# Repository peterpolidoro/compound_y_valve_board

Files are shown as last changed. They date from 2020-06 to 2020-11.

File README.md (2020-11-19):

- [Repository Information](#org6a90782)
  - [Description](#orgf515803)
- [Images](#org8e21772)
- [Schematic](#org4408de4)
- [Gerbers](#org2b33e62)
- [Bill of Materials](#org6bcd28f)
  - [PCB Parts](#orgb6b8d32)
  - [Supplemental Parts](#org0a79596)
  - [Vendor Parts Lists](#orgea142e0)
- [Supplemental Documentation](#org34a7f76)
  - [Assembly Instructions](#orgbe6a6db)
- [Manufacturing Archive](#org17d4580)

# Repository Information

-   **Name:** y\_arena\_valve\_controller
-   **Version:** 1.3
-   **License:** Open-Source Hardware
-   **URL:** <https://github.com/janelia-kicad/y_arena_valve_controller>
-   **Author:** Peter Polidoro
-   **Email:** peterpolidoro@gmail.com

## Description

This board controls the y-arena valves for the Turner lab.

## Documentation

<https://janelia-kicad.github.io/y_arena_odor_controller>

# Images

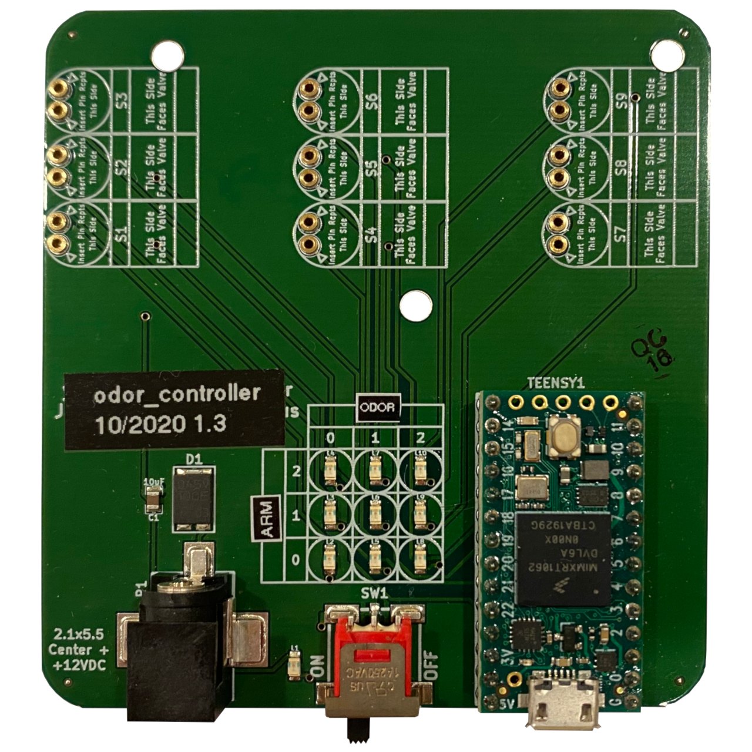
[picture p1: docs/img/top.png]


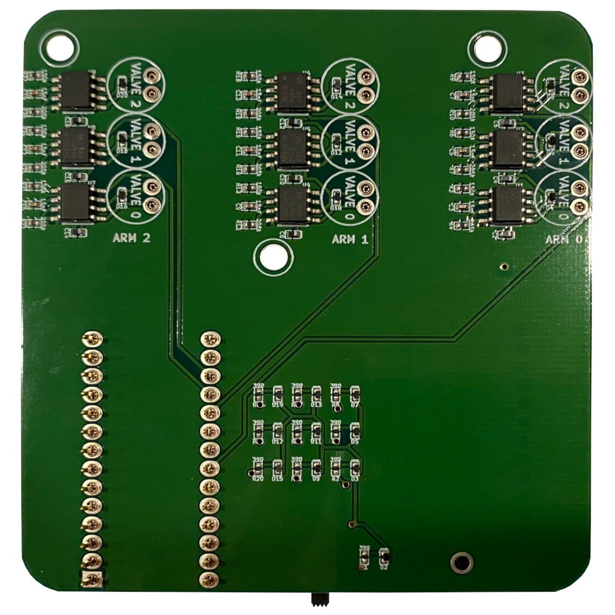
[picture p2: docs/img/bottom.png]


# Schematic

[./schematic/y\_arena\_valve\_controller.pdf](./schematic/y_arena_valve_controller.pdf)

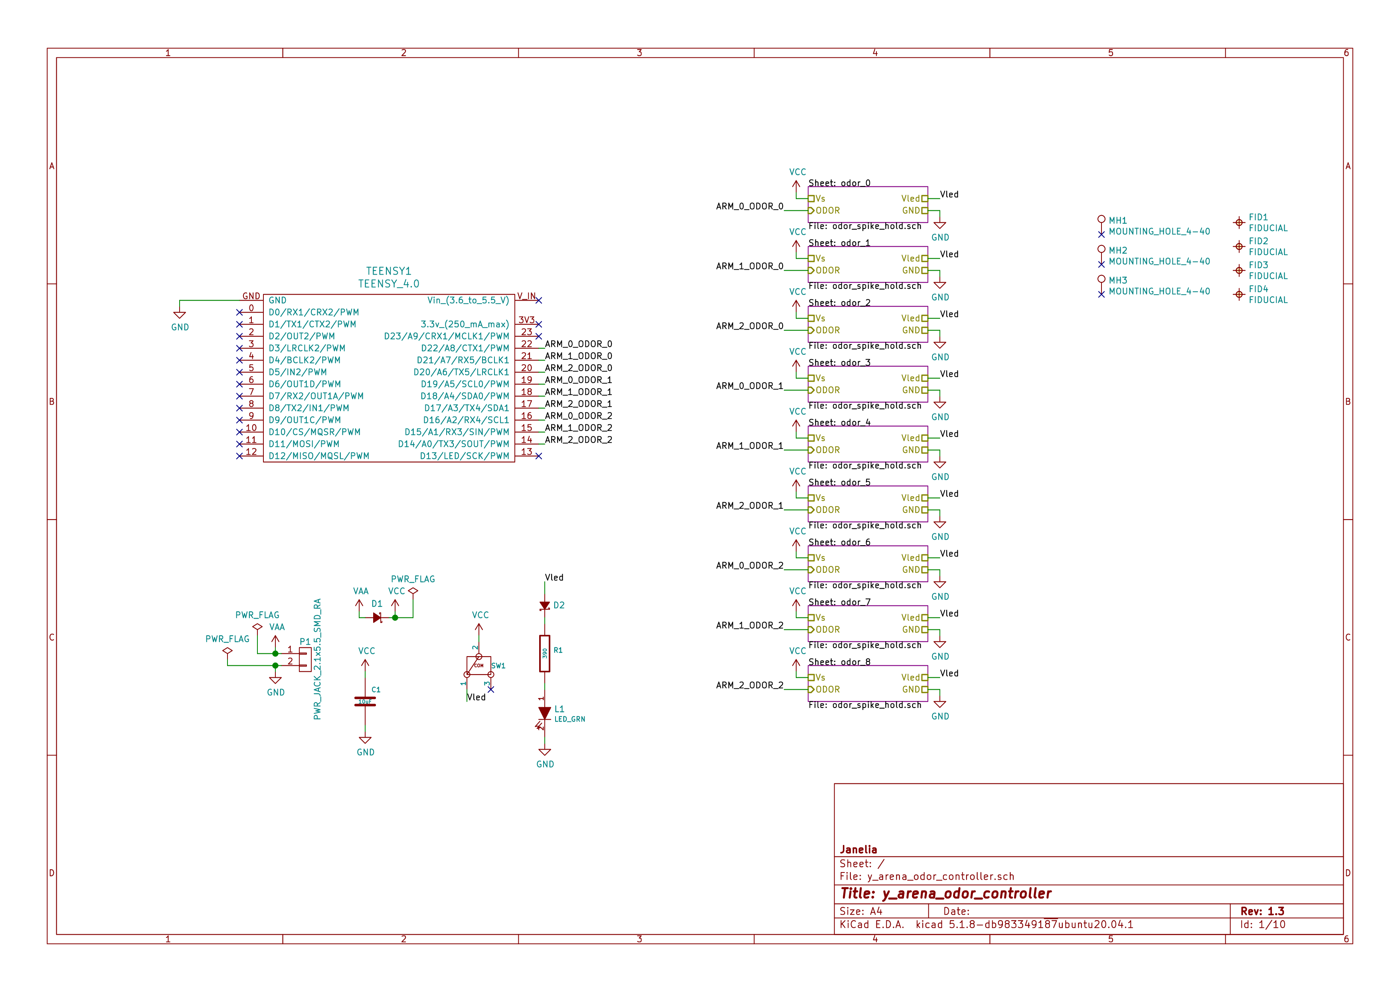
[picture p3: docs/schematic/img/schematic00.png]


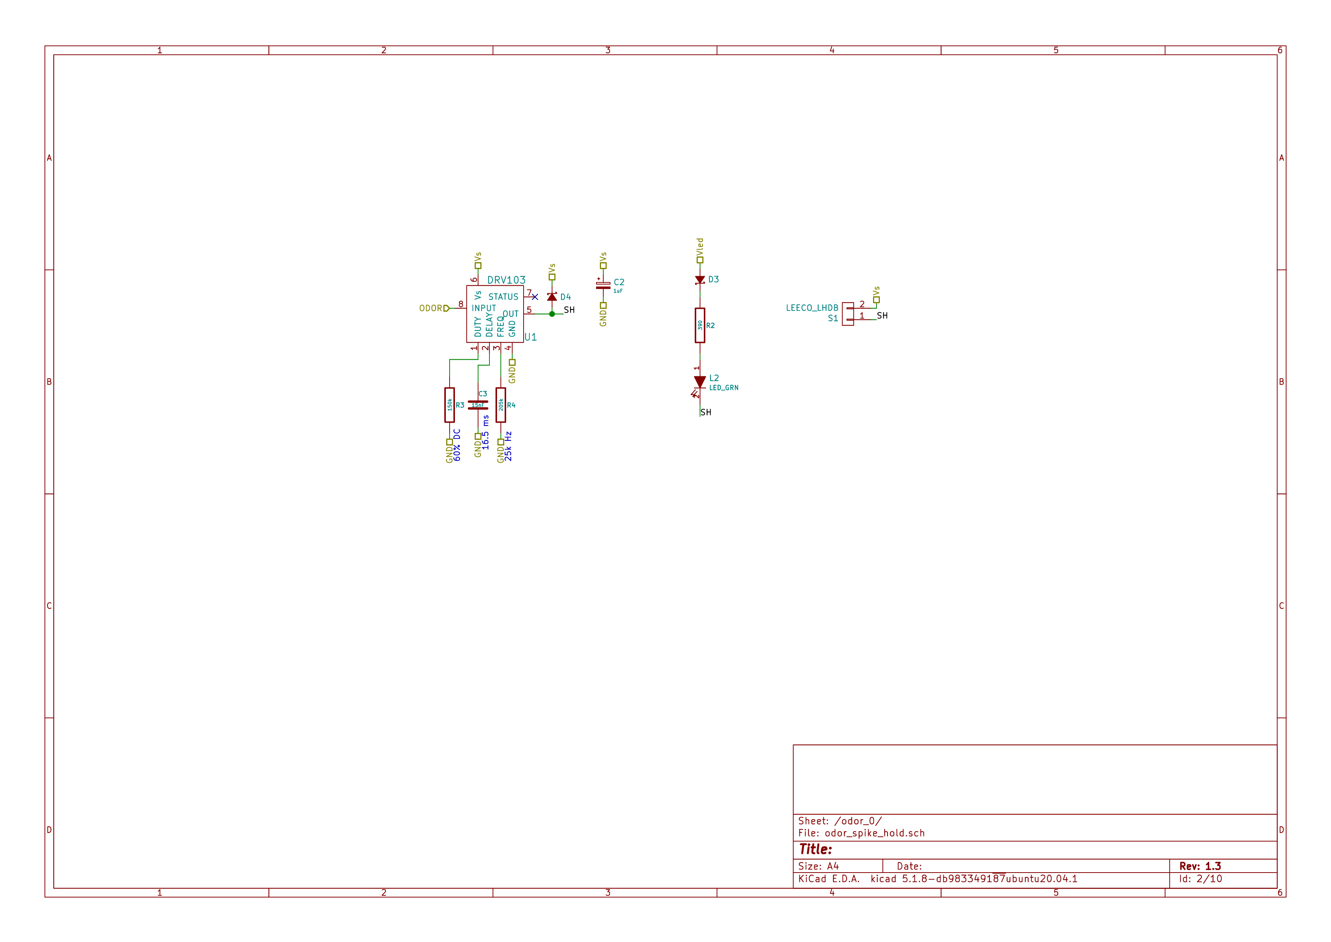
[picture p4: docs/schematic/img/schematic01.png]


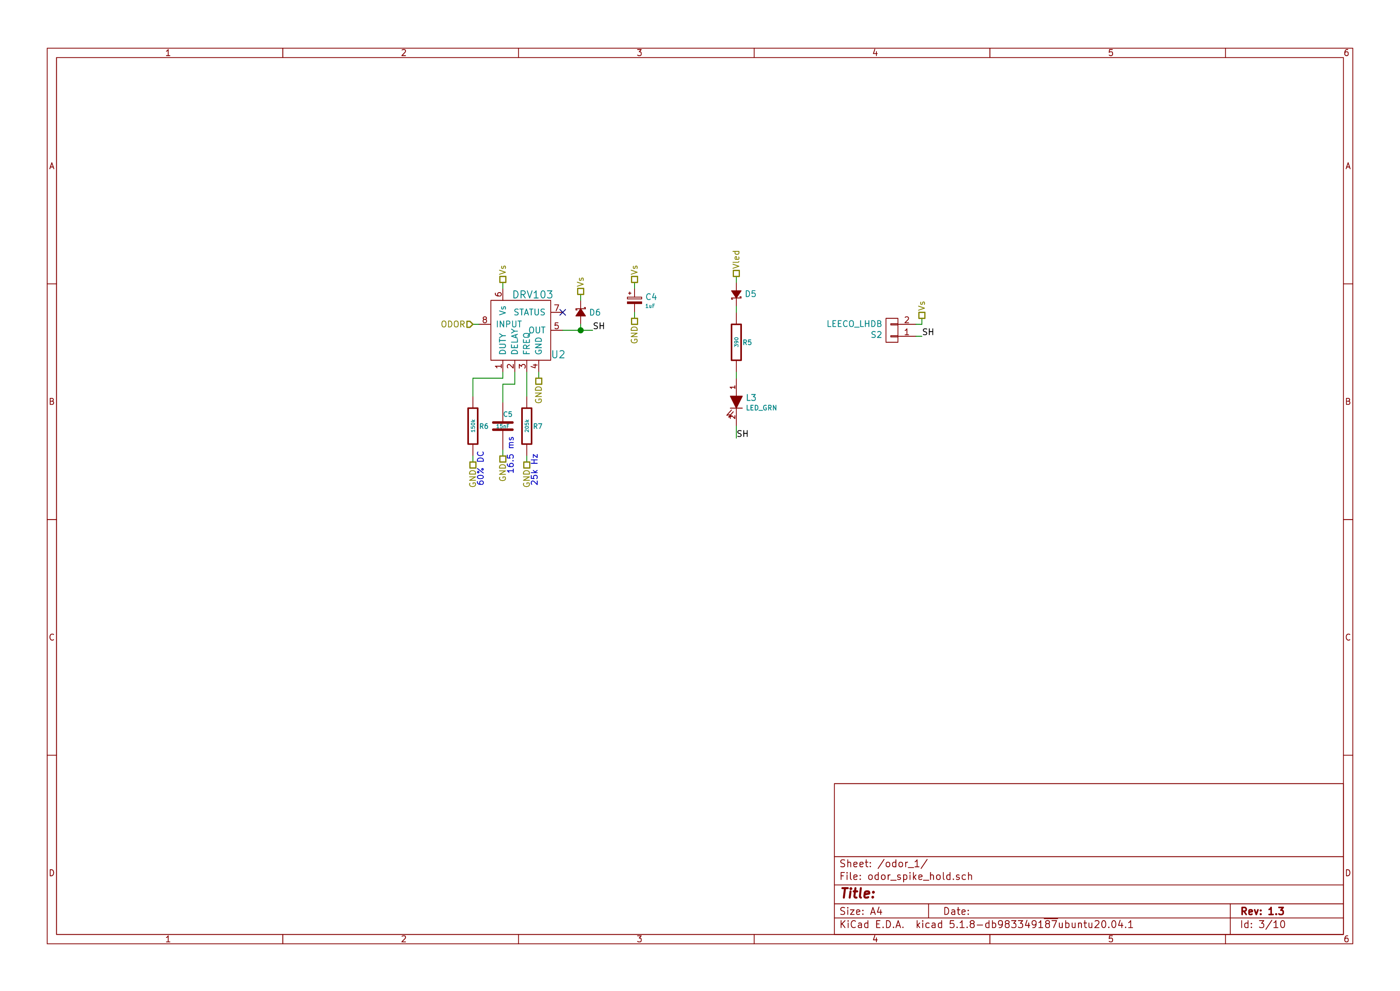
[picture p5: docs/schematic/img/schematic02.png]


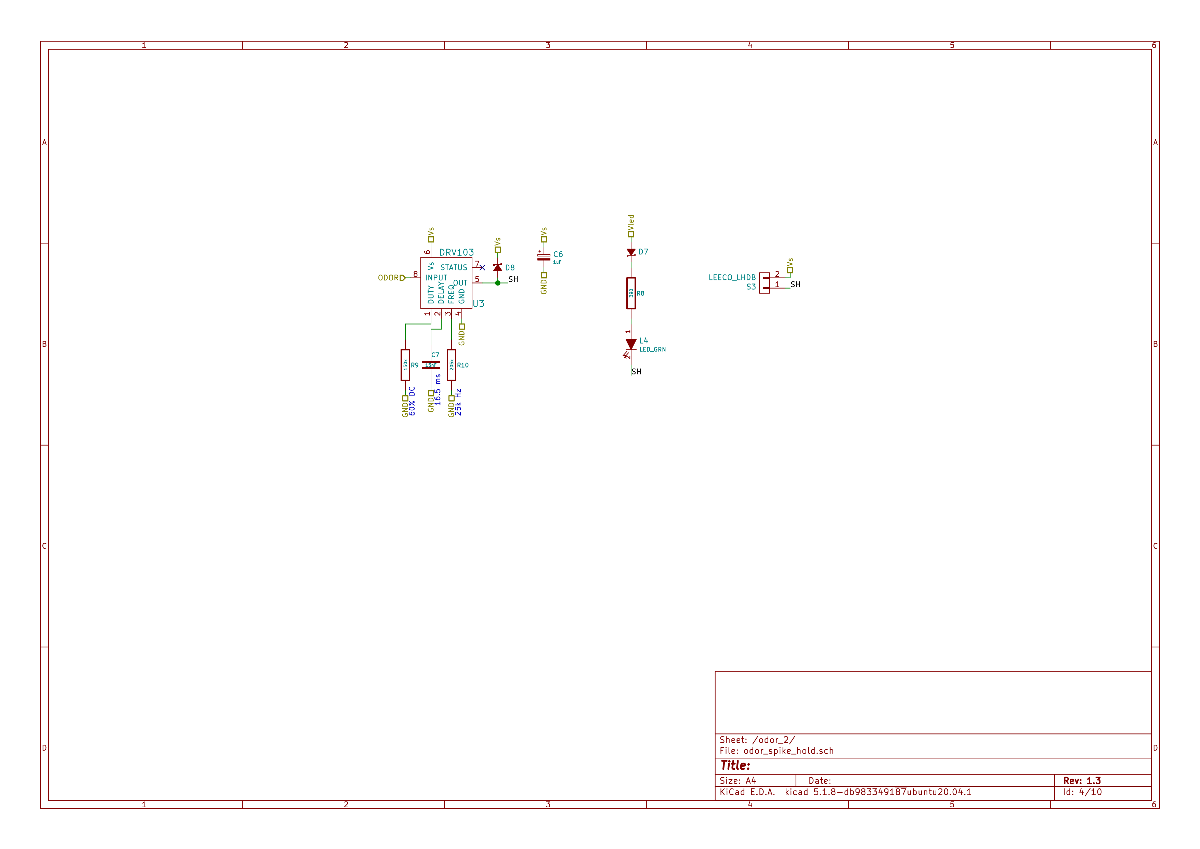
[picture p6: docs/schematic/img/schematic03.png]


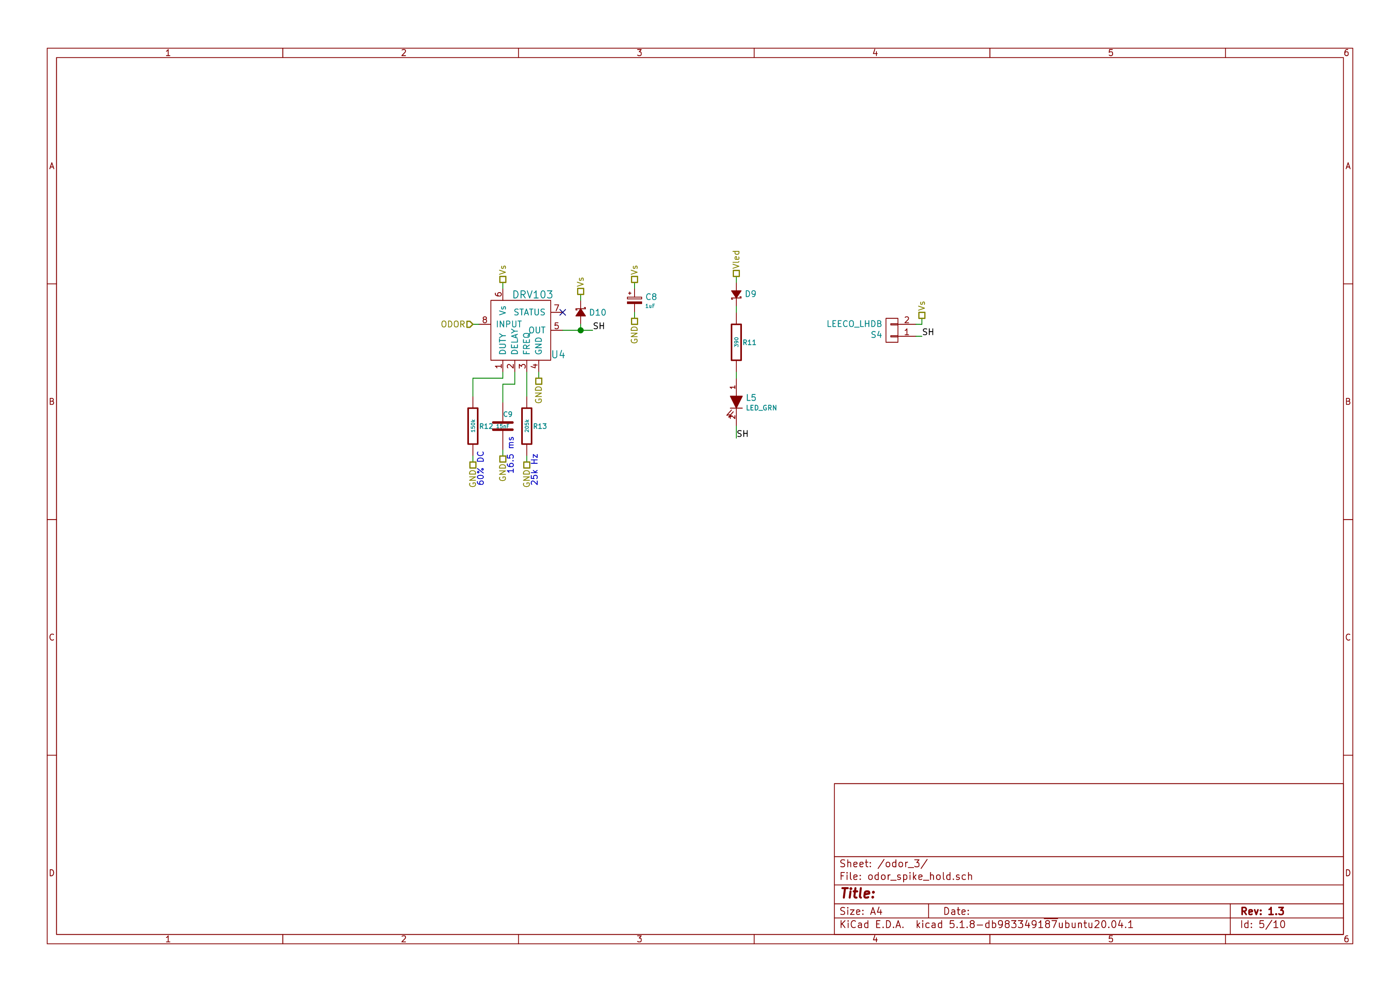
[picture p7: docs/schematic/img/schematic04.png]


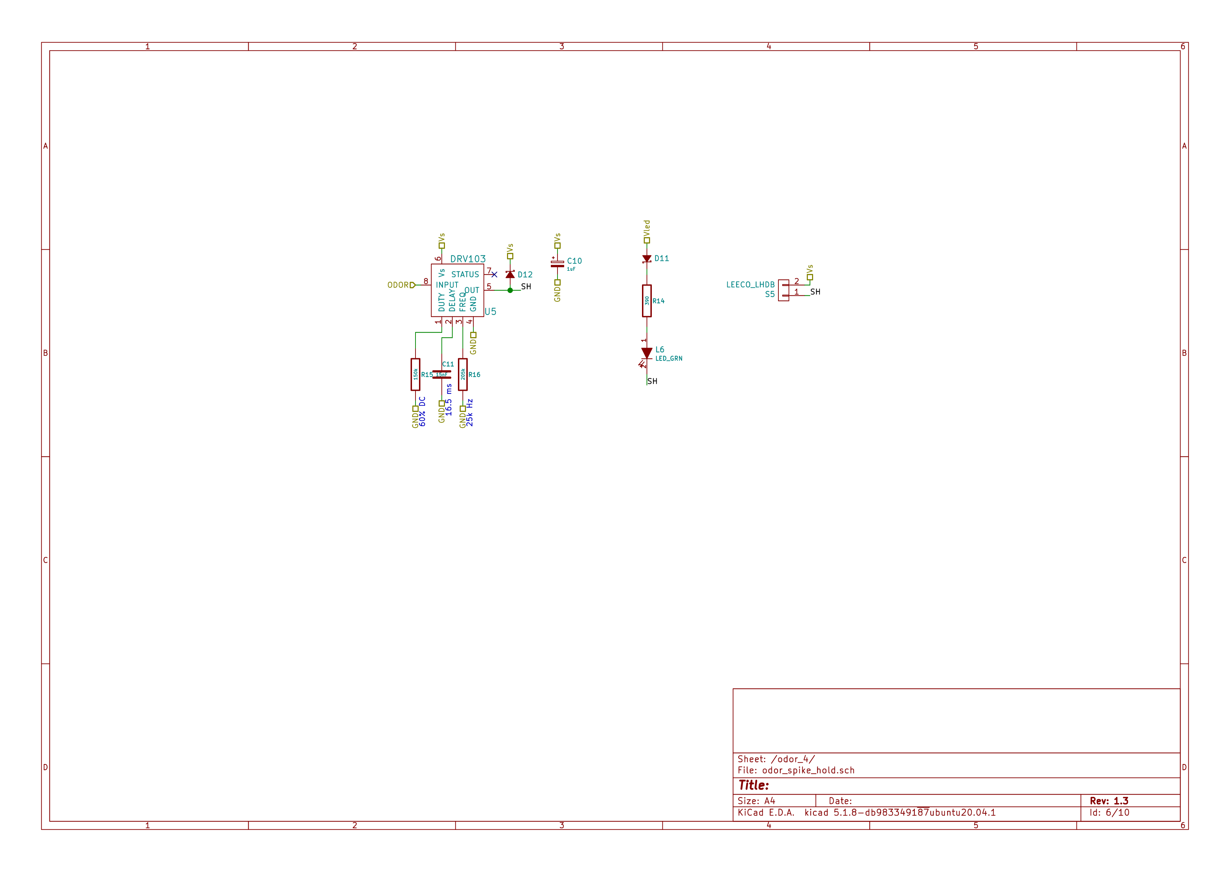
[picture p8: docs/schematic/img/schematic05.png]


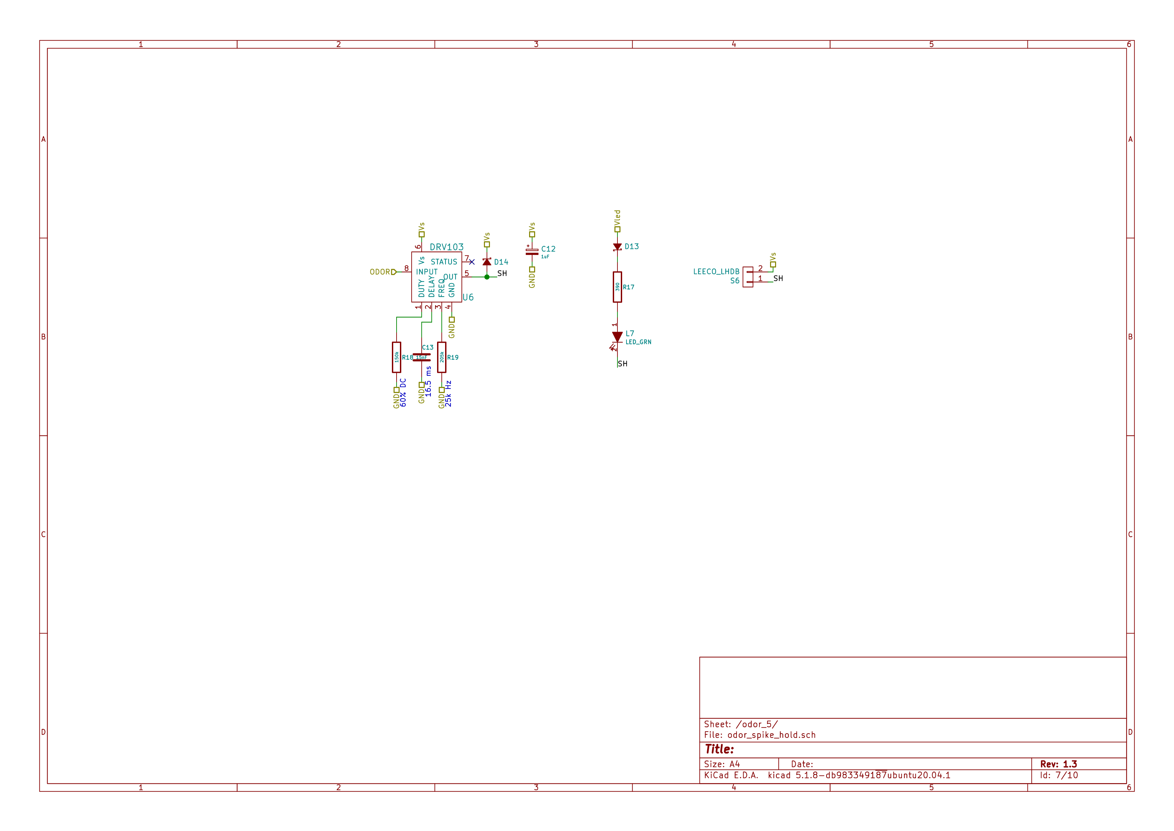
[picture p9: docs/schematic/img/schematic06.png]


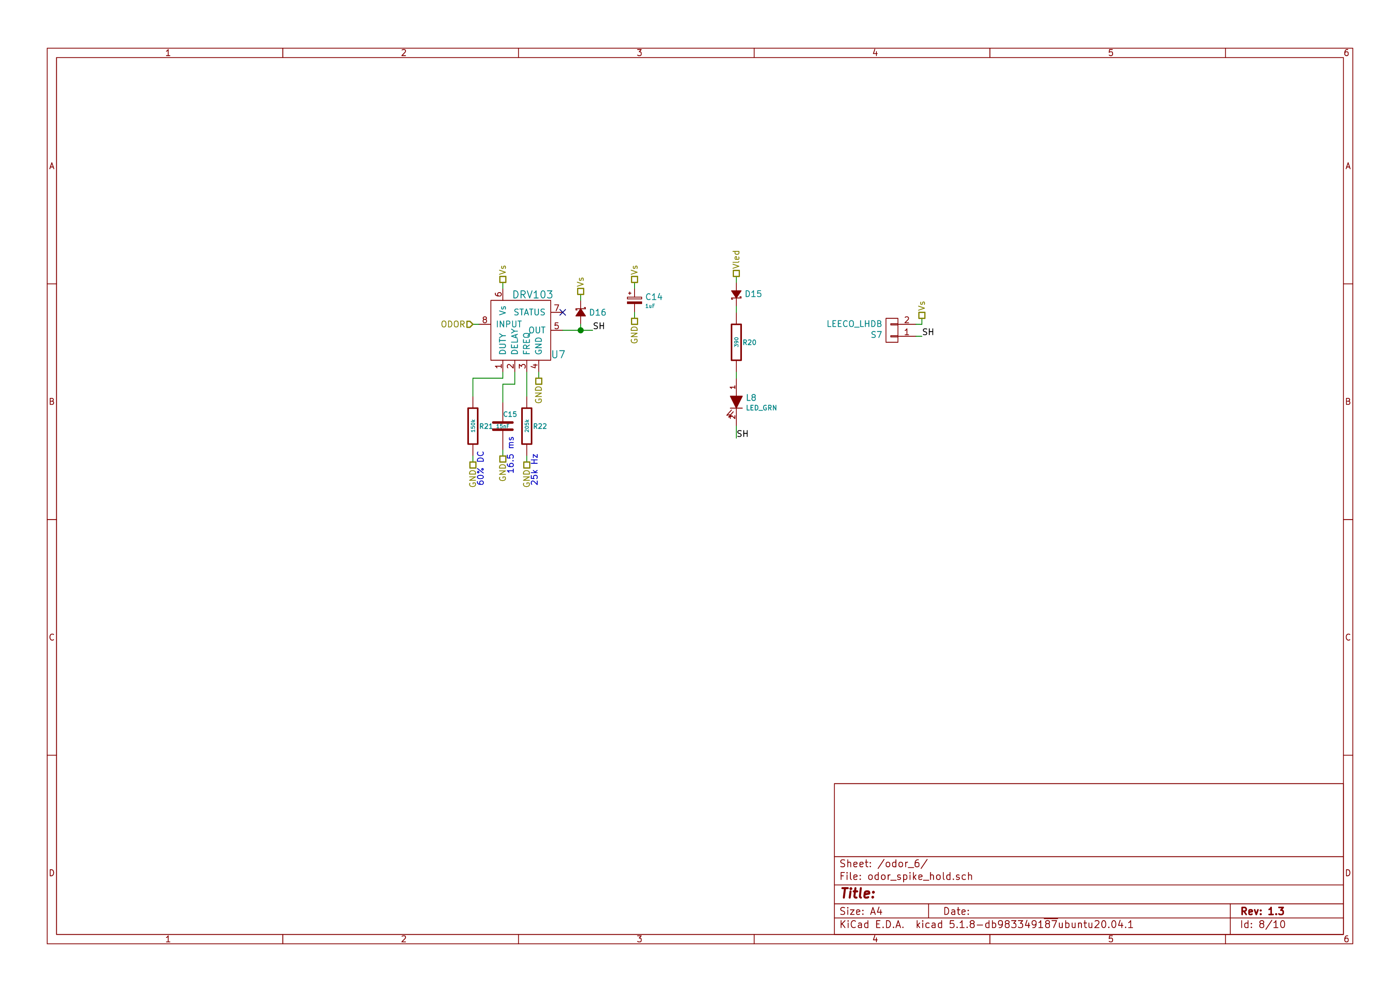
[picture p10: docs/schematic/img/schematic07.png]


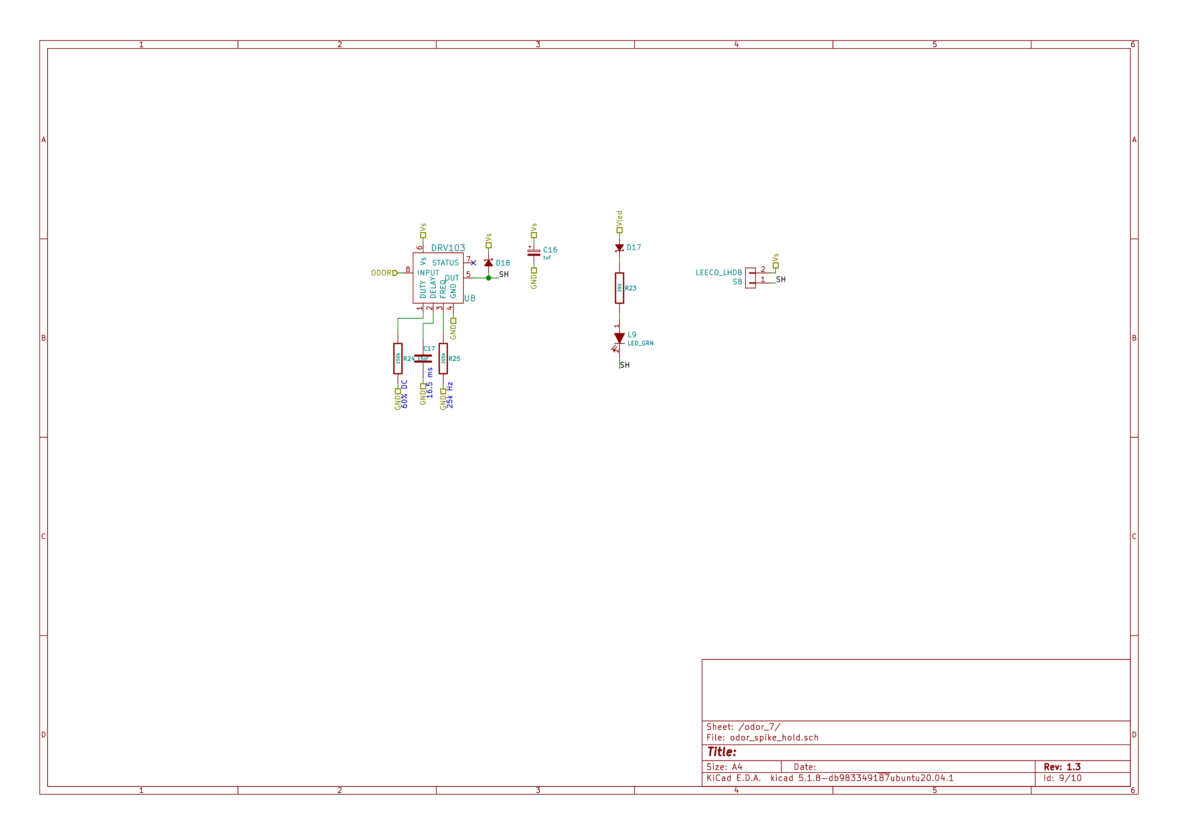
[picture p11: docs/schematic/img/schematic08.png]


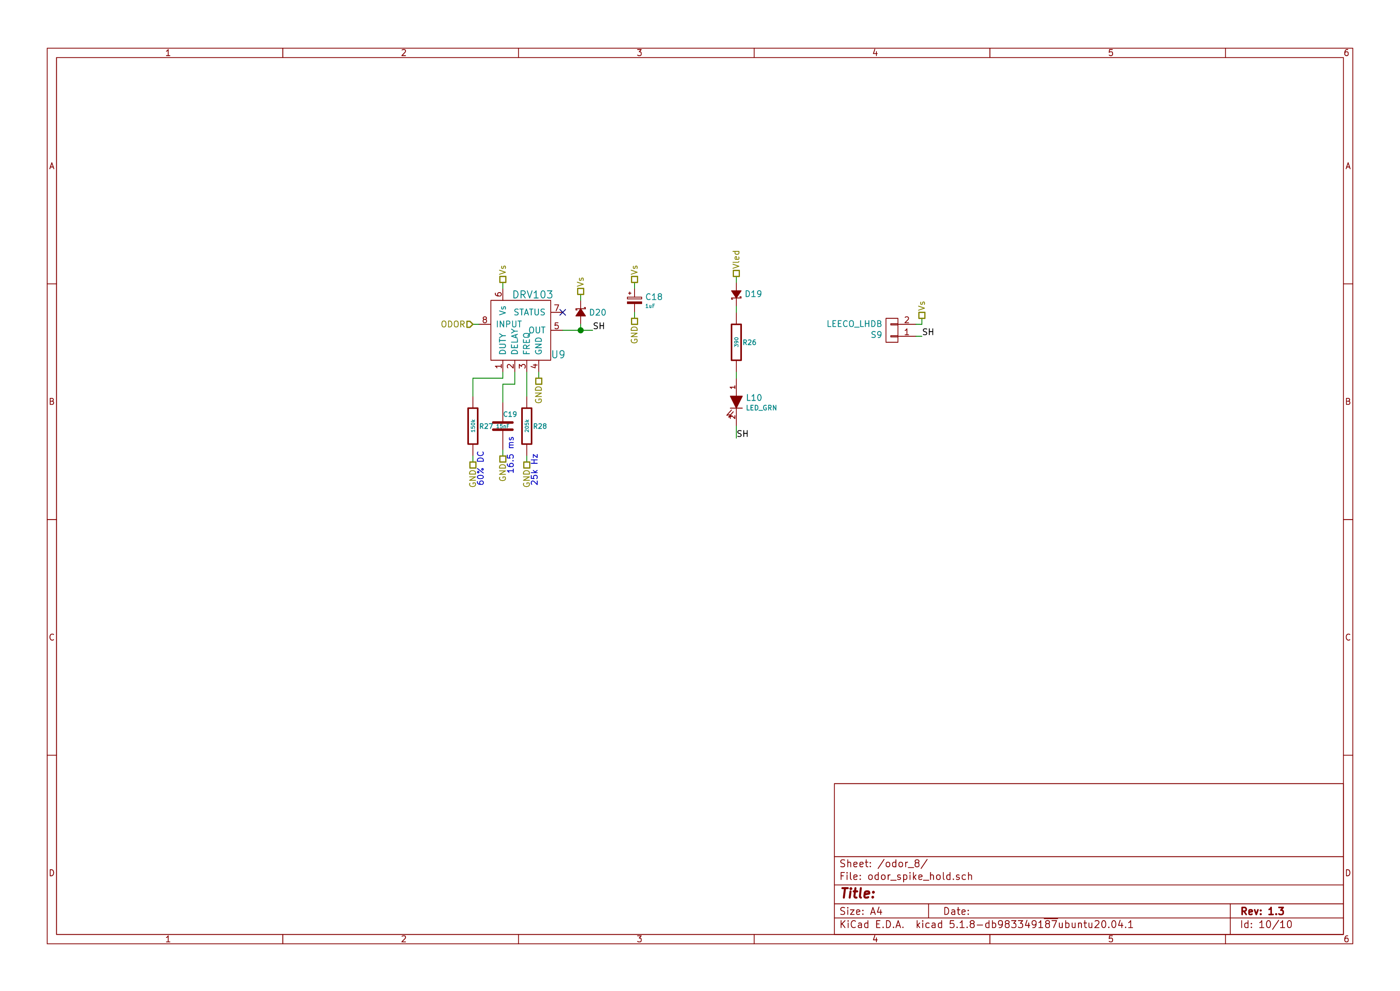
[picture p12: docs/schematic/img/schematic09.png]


# Gerbers

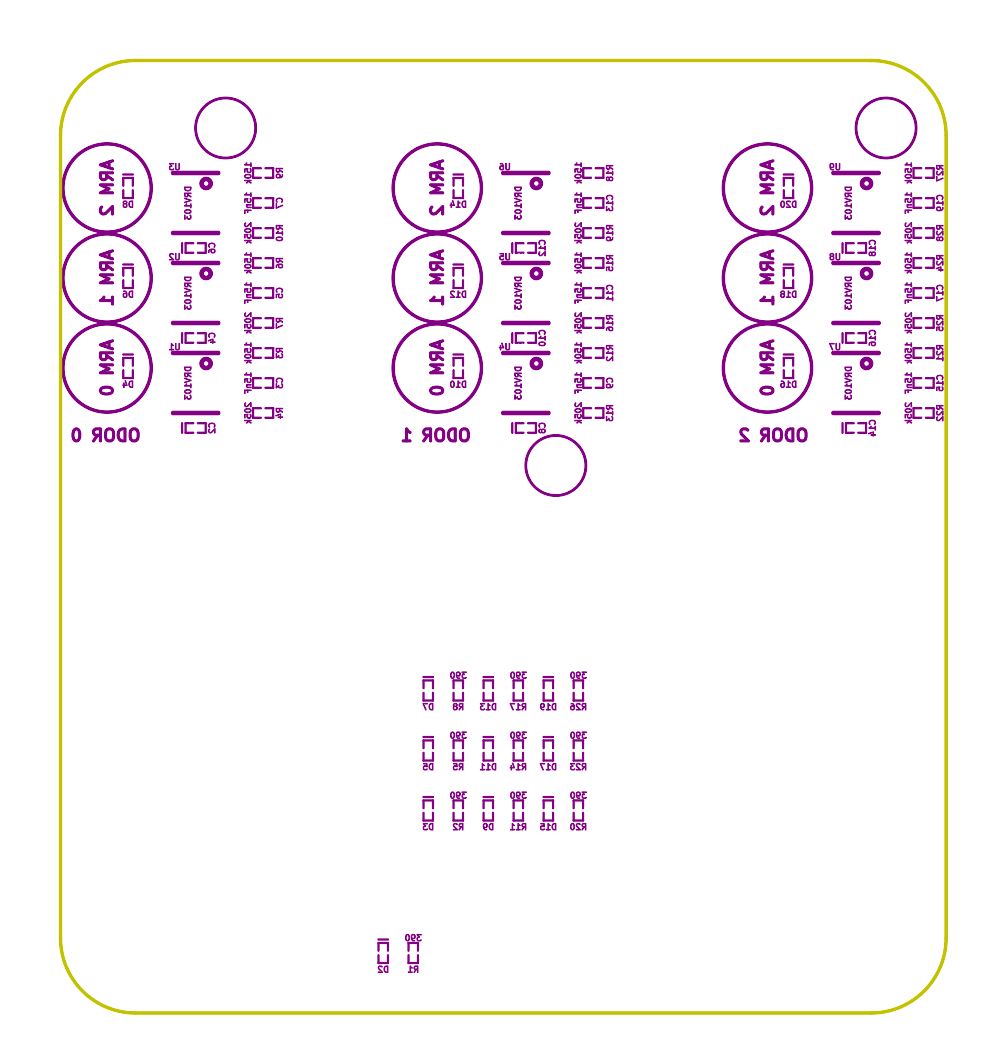
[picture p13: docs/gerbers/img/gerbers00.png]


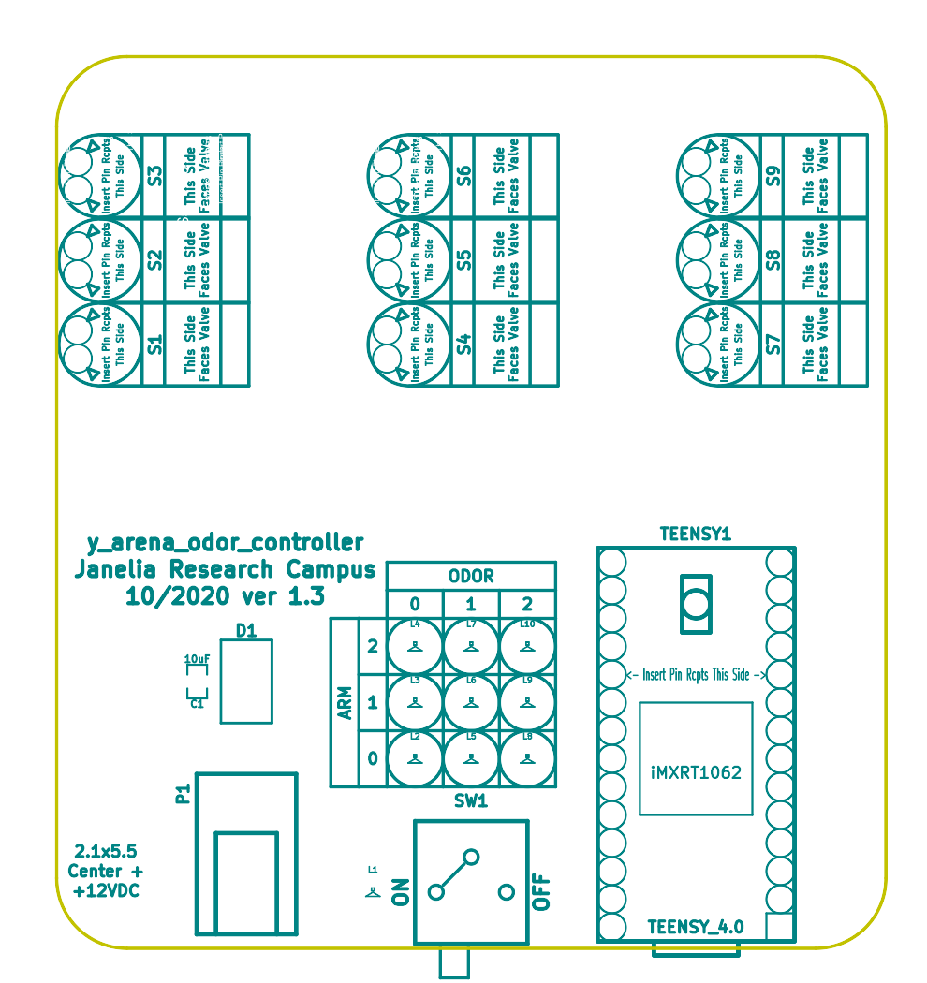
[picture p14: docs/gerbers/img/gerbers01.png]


# Bill of Materials

## PCB Parts

| Item | Reference(s)                        | Quantity | Manufacturer                    | Manufacturer Part Number | Vendor   | Vendor Part Number   | Description                    | Package            |
|---- |----------------------------------- |-------- |------------------------------- |------------------------ |-------- |-------------------- |------------------------------ |------------------ |
| 1    | C1                                  | 1        | TDK Corporation                 | C2012X5R1V106K085AC      | Digi-Key | 445-14417-1-ND       | CAP CER 10UF 35V X5R           | 0805 (2012 Metric) |
| 2    | C10 C12 C14 C16 C18 C2 C4 C6 C8     | 9        | Vishay Sprague                  | 298D105X0016K2T          | Digi-Key | 718-1618-1-ND        | CAP TANT 1UF 20% 16V           | 0402               |
| 3    | C11 C13 C15 C17 C19 C3 C5 C7 C9     | 9        | Murata Electronics              | GCM155R71H153JA55D       | Digi-Key | 490-16428-1-ND       | CAP CER 0.015UF 50V X7R 0402   | 0402               |
| 4    | D1                                  | 1        | Nexperia USA Inc.               | PMEG045V100EPDZ          | Digi-Key | 1727-1904-1-ND       | DIODE SCHOTTKY 45V 10A         | CFP15              |
| 5    | D10 D12 D14 D16 D18 D20 D4 D6 D8    | 9        | Comchip Technology              | CDBQR0230L               | Digi-Key | 641-1275-1-ND        | DIODE SCHOTTKY 30V 200MA       | 0402               |
| 6    | D11 D13 D15 D17 D19 D3 D5 D7 D9 D2  | 10       | Diodes Incorporated             | BAS116LPH4-7B            | Digi-Key | BAS116LPH4-7BDICT-ND | DIODE GEN PURP 85V 215MA 2DFN  | 0402               |
| 7    | L1 L10 L2 L3 L4 L5 L6 L7 L8 L9      | 10       | Lite-On Inc.                    | LTST-C170GKT             | Digi-Key | 160-1179-1-ND        | LED GREEN CLEAR SMD            | 0805 (2012 Metric) |
| 8    | P1                                  | 1        | CUI Devices                     | PJ-036AH-SMT-TR          | Digi-Key | CP-036AHPJCT-ND      | CONN PWR JACK 2X5.5MM SOLDER   |                    |
| 9    | R1 R11 R14 R17 R2 R20 R23 R26 R5 R8 | 10       | Panasonic Electronic Components | ERJ-PA2J391X             | Digi-Key | P124568CT-ND         | RES SMD 390 OHM 5% 1/5W        | 0402               |
| 10   | R10 R13 R16 R19 R22 R25 R28 R4 R7   | 9        | Panasonic Electronic Components | ERJ-2RKF2053X            | Digi-Key | P205KLCT-ND          | RES SMD 205K OHM 1% 1/10W 0402 | 0402               |
| 11   | R12 R15 R18 R21 R24 R27 R3 R6 R9    | 9        | Panasonic Electronic Components | ERJ-2RKF1503X            | Digi-Key | P150KLCT-ND          | RES SMD 150K OHM 1% 1/10W 0402 | 0402               |
| 12   | S1 S2 S3 S4 S5 S6 S7 S8 S9 TEENSY1  | 46       | Mill-Max Manufacturing Corp     | 0305-0-15-15-47-27-10-0  | Digi-Key | ED90331-ND           | CONN PIN RCPT .025-.037 SOLDER |                    |
| 13   | SW1                                 | 1        | E-Switch                        | 500ASSP1SM6QE            | Digi-Key | EG5810CT-ND          | SWITCH SLIDE SPDT 3A 120V      |                    |
| 14   | U1 U2 U3 U4 U5 U6 U7 U8 U9          | 9        | Texas Instruments               | DRV103U                  | Digi-Key | 296-11622-ND         | IC LO-SIDE DRIVER PWM 8SOIC    | 8SOIC              |
|      | FID1 FID2 FID3 FID4 MH1 MH2 MH3     | 7        |                                 |                          |          |                      |                                |                    |

## Supplemental Parts

| Item | Quantity | Manufacturer                 | Manufacturer Part Number        | Vendor   | Vendor Part Number                 | Description                      |
|---- |-------- |---------------------------- |------------------------------- |-------- |---------------------------------- |-------------------------------- |
| 1    | 1        | SparkFun Electronics         | DEV-15583                       | Digi-Key | 1568-DEV-15583-ND                  | TEENSY 4.0                       |
| 2    | 2        | Molex                        | 0022284146                      | Digi-Key | WM24210-ND                         | CONN HEADER VERT 14POS 2.54MM    |
| 3    | 1        | Qualtek                      | 3021075-03                      | Digi-Key | Q1223-ND                           | USB 2.0 A MALE TO USB 2.0 MICRO  |
| 4    | 1        | Tripp Lite                   | U222-004-R                      | Digi-Key | TL430-ND                           | HUB USB 4-PORT 2.0 & 1.1         |
| 5    | 1        | MEAN WELL USA Inc.           | GST60A12-P1J                    | Digi-Key | 1866-2149-ND                       | AC/DC DESKTOP ADAPTER 12V 60W    |
| 6    | 1        | MEAN WELL USA Inc.           | YP12+YC12                       | Digi-Key | 1866-5006-ND                       | CORD IEC 320-C13 6FT BLACK       |
| 7    | 1        | Tensility International Corp | 10-02739                        | Digi-Key | 839-1474-ND                        | SPLITTER 5.5X2.1MM F TO X4 M     |
| 8    | 1        | Tensility International Corp | CA-2219                         | Digi-Key | CP-2219-ND                         | CABLE ASSY 5.5X2.1MM M/F R/A 3FT |
| 9    | 1        | Raspberry Pi                 | RASPBERRY PI 4B/4GB             | Digi-Key | 1690-RASPBERRYPI4B/4GB-ND          | RASPBERRY PI 4B/4GB              |
| 10   | 1        | Raspberry Pi                 | RPI USB-C POWER SUPPLY BLACK US | Digi-Key | 1690-RPIUSB-CPOWERSUPPLYBLACKUS-ND | RPI USB-C POWER SUPPLY BLACK US  |
| 11   | 1        | Raspberry Pi                 | RASPBERRY PI 4 CASE BLACK/GREY  | Digi-Key | 1690-RASPBERRYPI4CASEBLACK/GREY-ND | RASPBERRY PI 4 CASE BLACK/GREY   |
| 12   | 1        | Raspberry Pi                 | 8997466                         | Digi-Key | 1690-1007-ND                       | RASPBERRY PI 7" TOUCH SCREEN LCD |
| 13   | 1        | ATP Electronics Inc          | AF32GUD3-OEM                    | Digi-Key | AF32GUD3-OEM-ND                    | MEM CARD MICROSD 32GB CLS 10 MLC |
| 14   | 1        | Tripp Lite                   | U352-000-MD                     | Digi-Key | TL825-ND                           | USB 3.0 MULTI-DRIVE SD CF MS     |
| 15   | 1        | Tripp Lite                   | U336-000-R                      | Digi-Key | TL824-ND                           | USB 3.0 TO ETHERNET ADAPTER      |
| 16   | 1        | Assmann WSW Components       | A-MCSSP60010/B                  | Digi-Key | AE10190-ND                         | CABLE MOD 8P8C PLUG-PLUG 3.28FT  |

## Vendor Parts Lists

[./bom/Digi-Key\_parts.csv](./bom/Digi-Key_parts.csv)

[./bom/supplemental\_Digi-Key\_parts.csv](./bom/supplemental_Digi-Key_parts.csv)

# Supplemental Documentation

## Assembly Instructions

Solder surface mount and through hole components onto the pcb.

# Manufacturing Archive

Send manufacturing zip file to your favorite PCB manufacturer for fabrication.

[./manufacturing/y\_arena\_valve\_controller\_v1.3.zip](./manufacturing/y_arena_valve_controller_v1.3.zip)

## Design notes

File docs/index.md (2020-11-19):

This board controls the y-arena odors for the Janelia Turner lab.





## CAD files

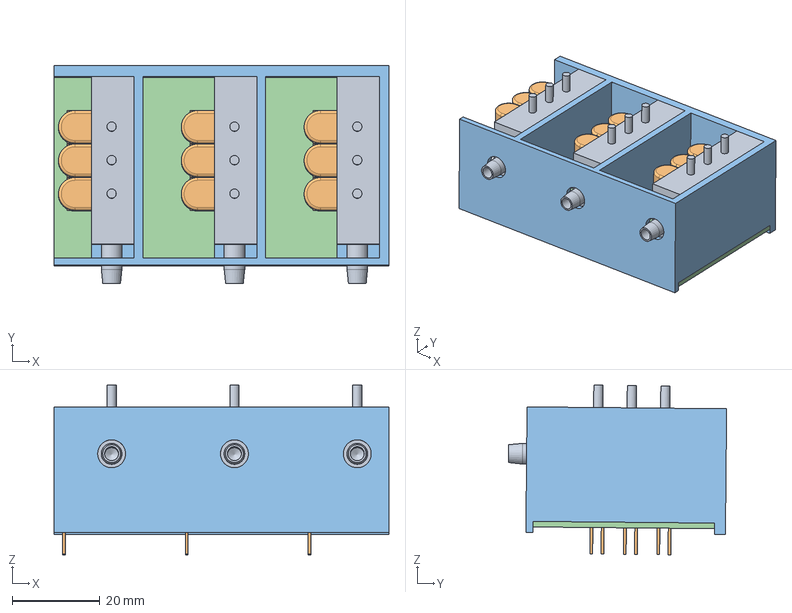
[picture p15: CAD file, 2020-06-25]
mechanical/valve_assembly.stp
76.2 x 49.6 x 38.6 mm
LFMX0527550B 3X MANIFOLD x 3
LHDB0052015B 2 PORT FACE MOUNT VALVE x 9
VALVE HOLDER
PERP VALVE PCB

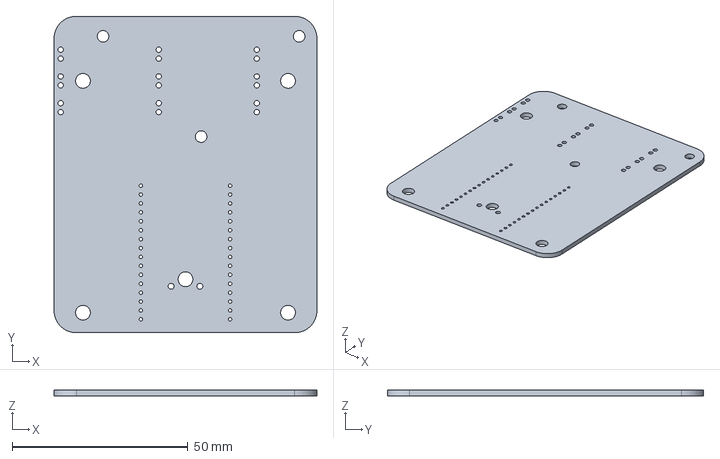
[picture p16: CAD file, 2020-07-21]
gerbers/y_arena_valve_controller.step
74.9 x 90.2 x 1.60 mm

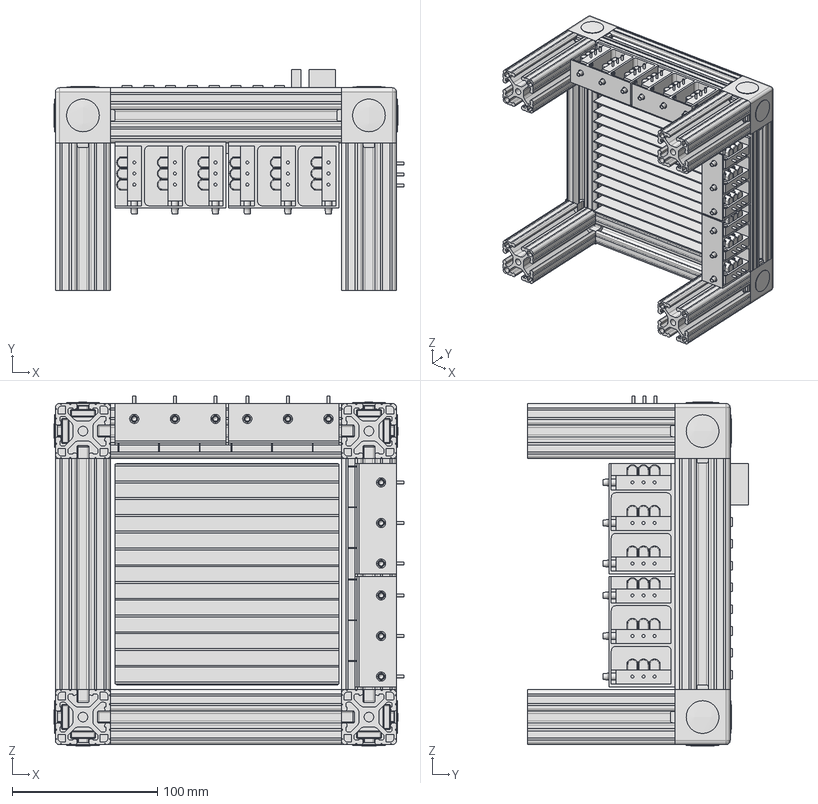
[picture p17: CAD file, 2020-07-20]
mechanical/4_Y_ARENA_STAND.stp
240.9 x 152.4 x 240.9 mm
3,5in x 1,5in T-SLOTTED FRAMING x 4
6in x 1,5in T-SLOTTED FRAMING x 4
6x6 HEATSINK
PCB RGB J007017
LFMX0527550B 3X MANIFOLD x 12
LHDB0052015B 2 PORT FACE MOUNT VALVE x 36
VALVE HOLDER x 4
PERP VALVE PCB x 4
47065T245_ALUMINUM T-SLOTTED FRAMING EXTRUSION x 4

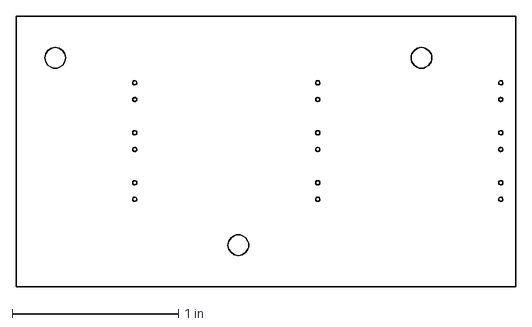
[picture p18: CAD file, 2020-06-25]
mechanical/valve_pcb.dxf
3.00 x 1.62 in

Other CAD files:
mechanical/y_arena_valve_controller.stp

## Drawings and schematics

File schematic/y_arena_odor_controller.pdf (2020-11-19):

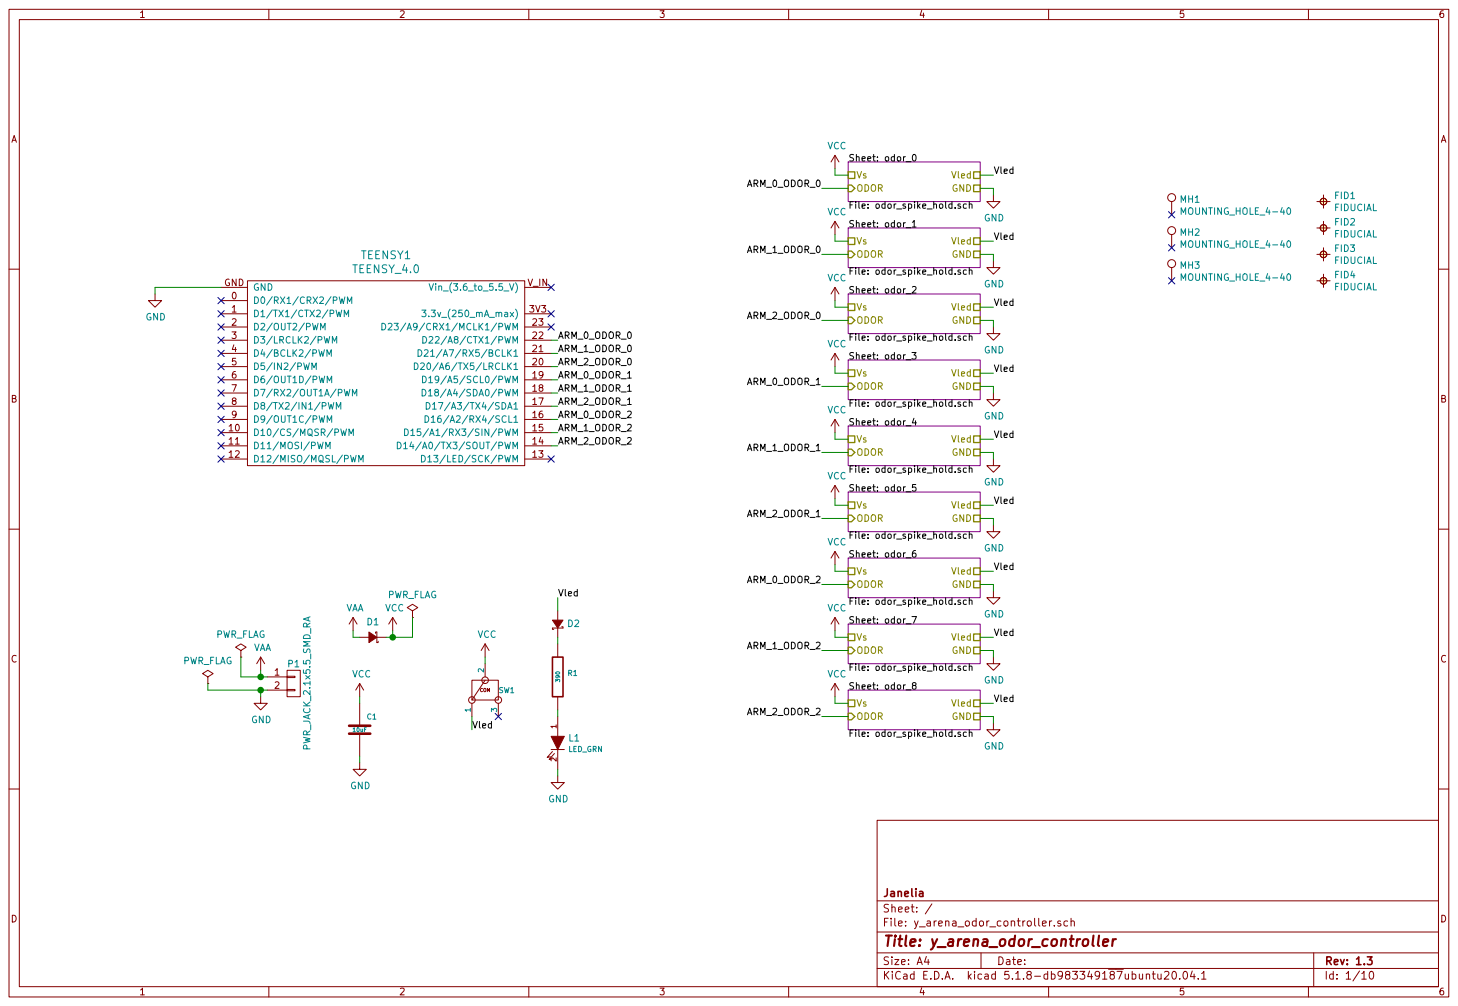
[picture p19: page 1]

File: y_arena_odor_controller.sch Sheet: / Janelia

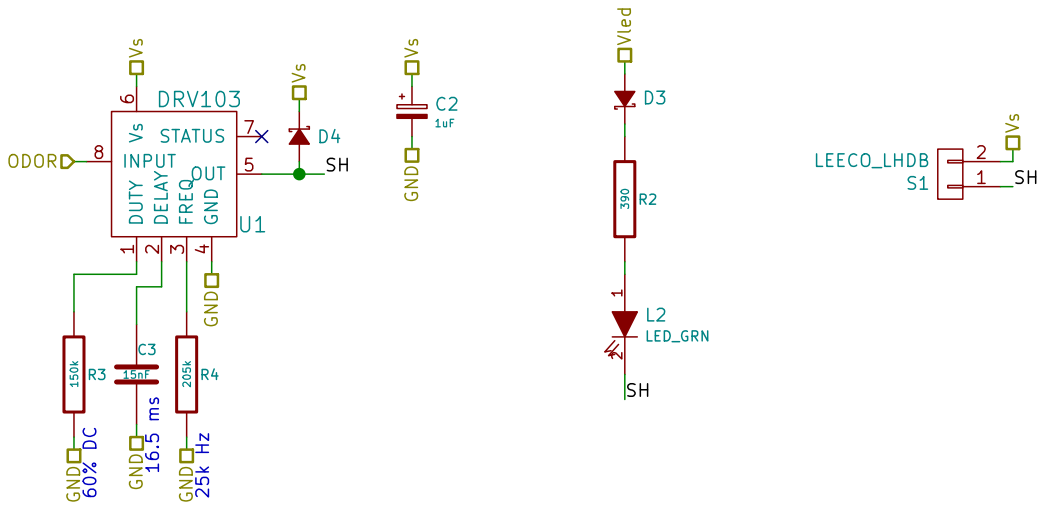
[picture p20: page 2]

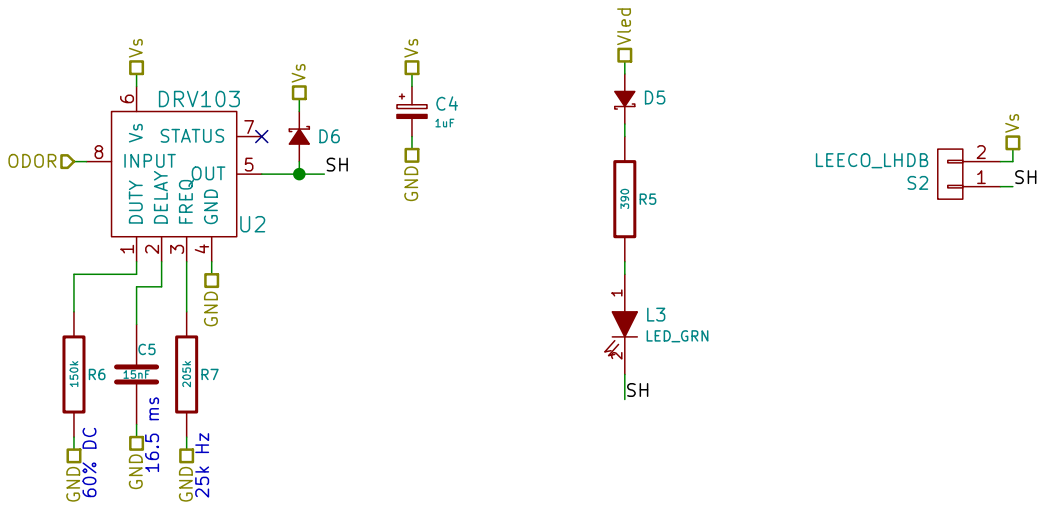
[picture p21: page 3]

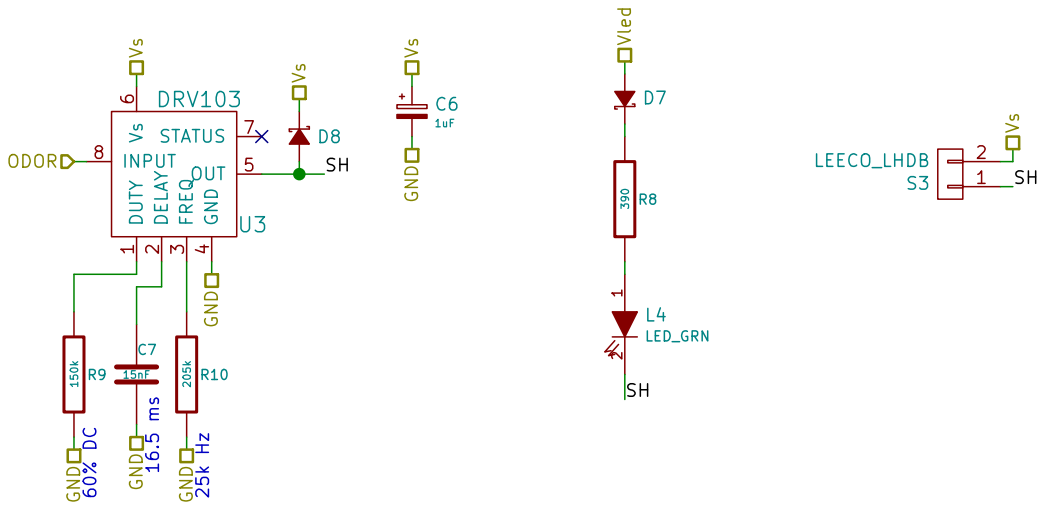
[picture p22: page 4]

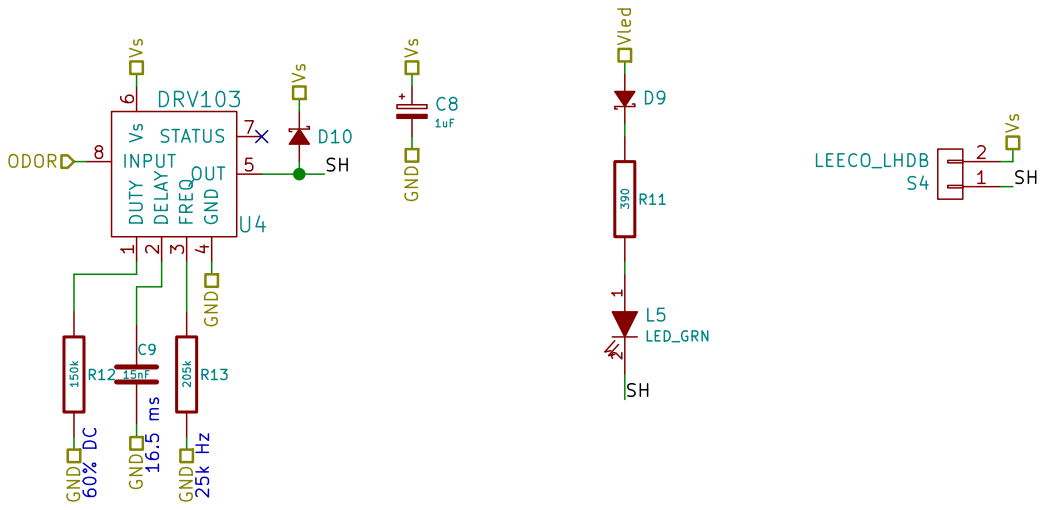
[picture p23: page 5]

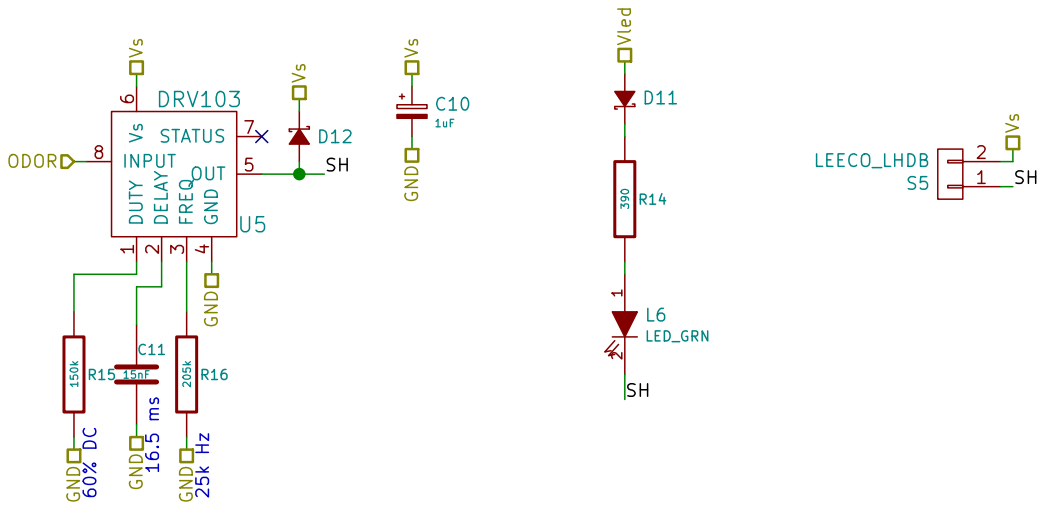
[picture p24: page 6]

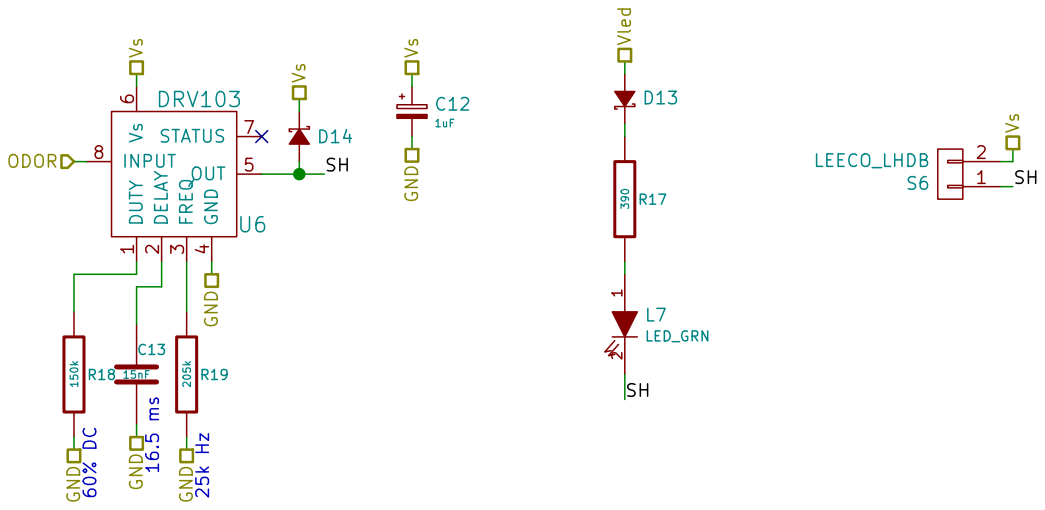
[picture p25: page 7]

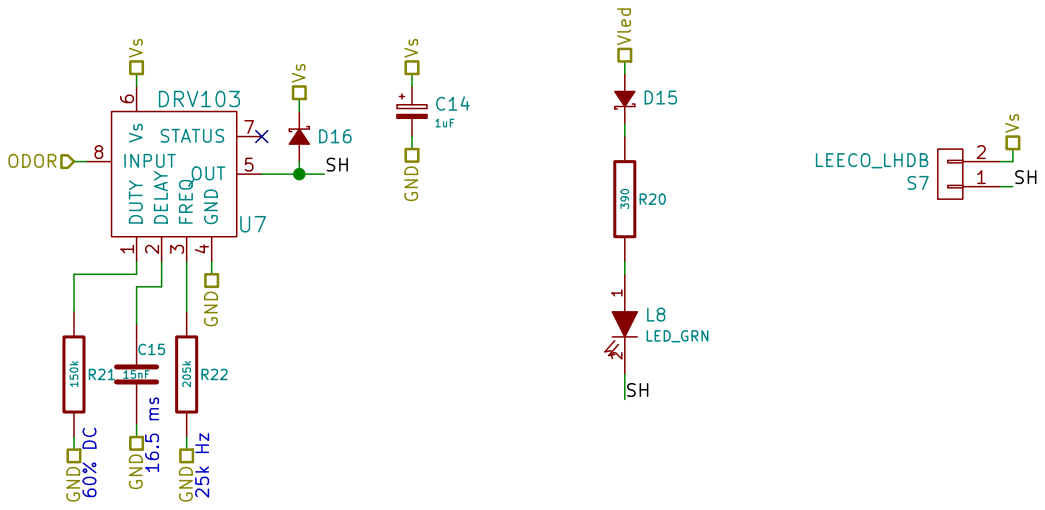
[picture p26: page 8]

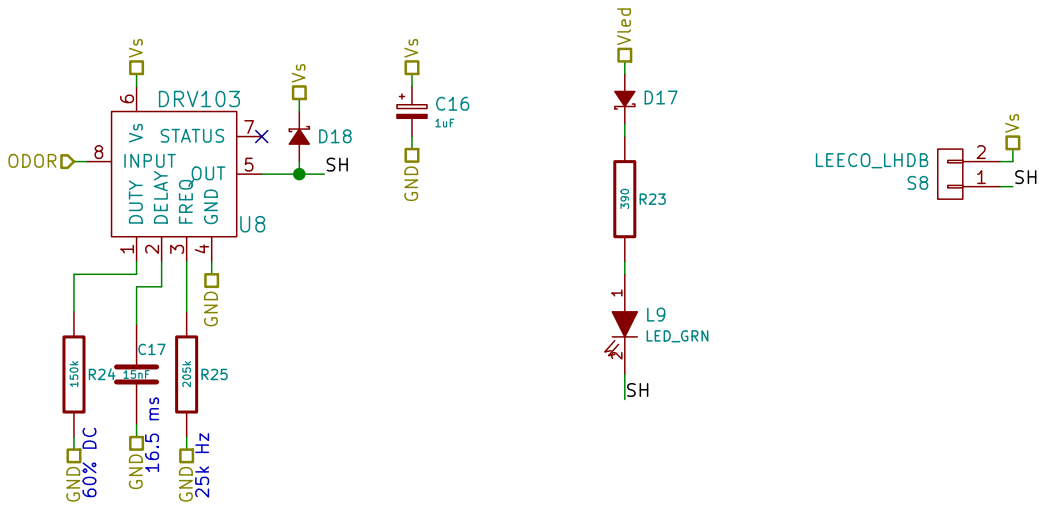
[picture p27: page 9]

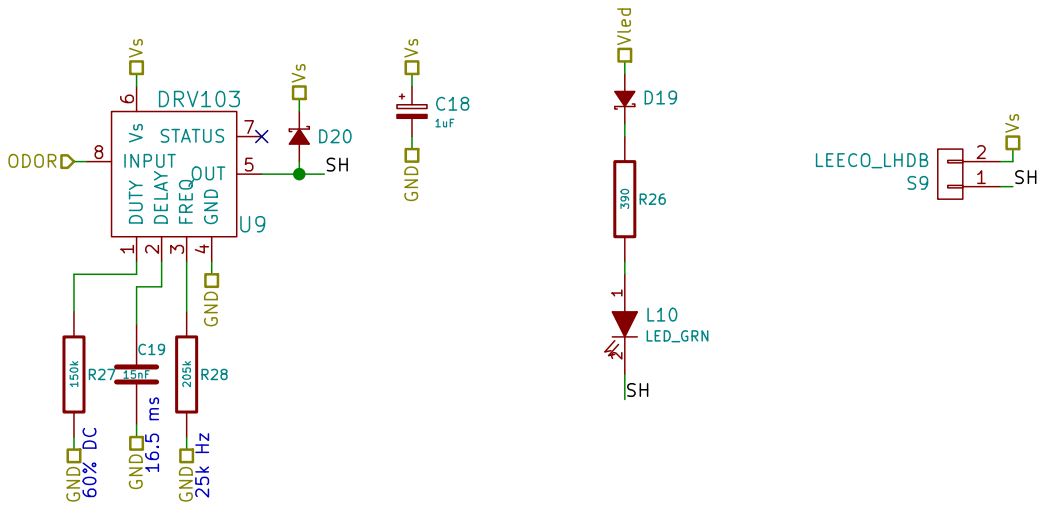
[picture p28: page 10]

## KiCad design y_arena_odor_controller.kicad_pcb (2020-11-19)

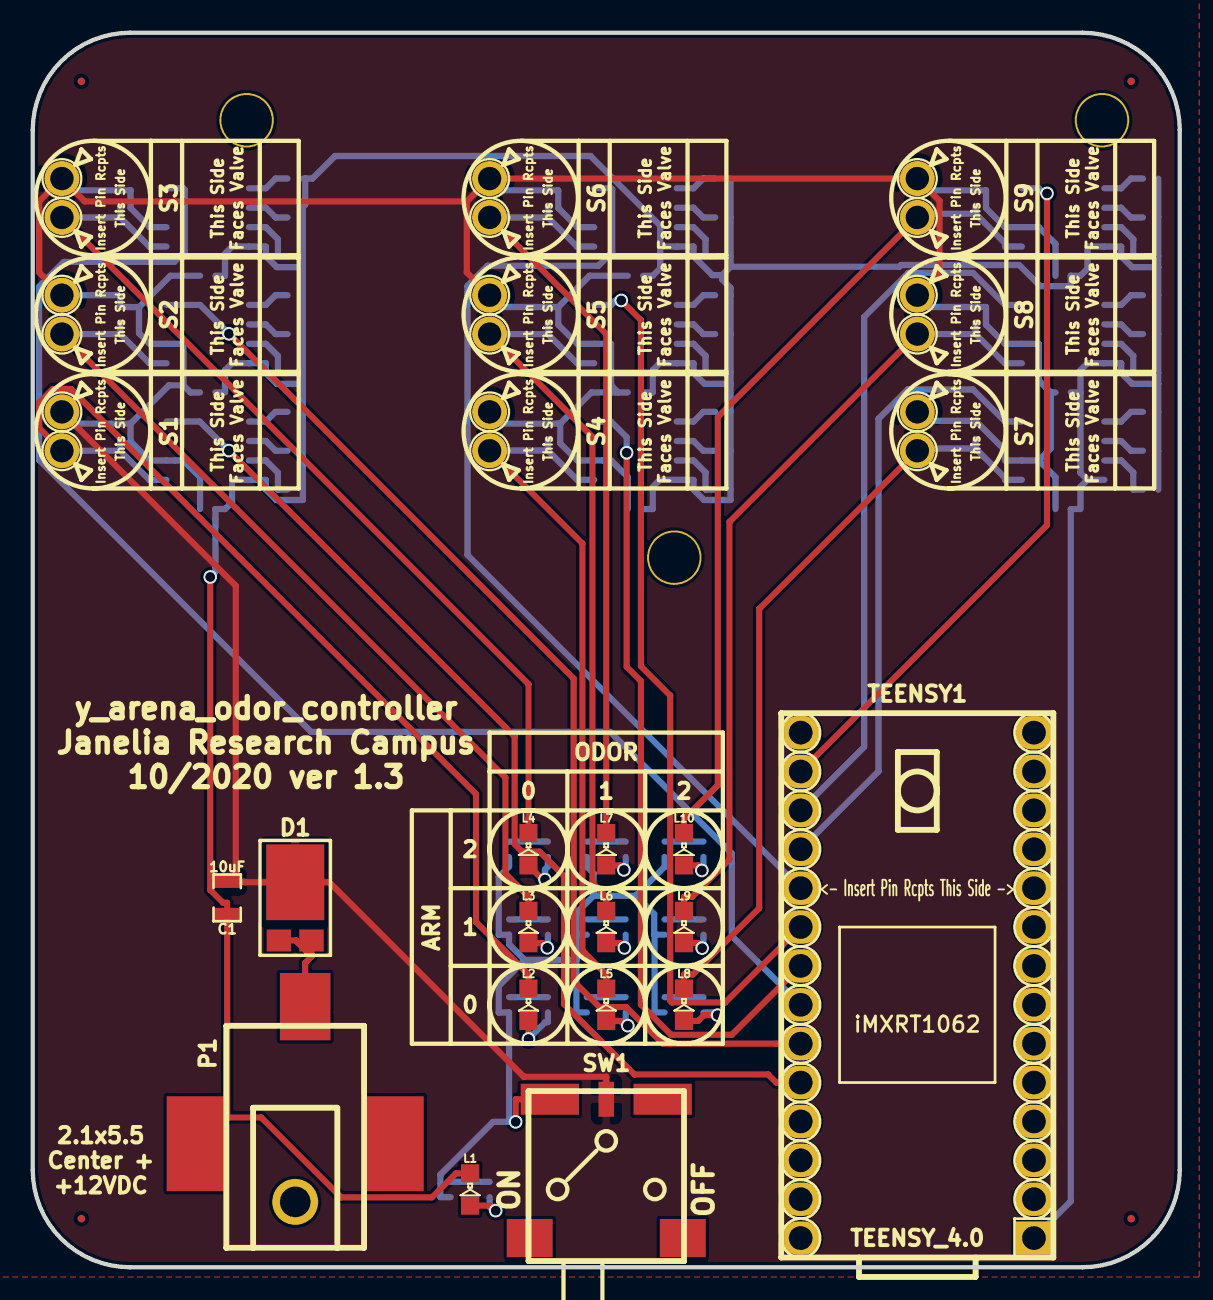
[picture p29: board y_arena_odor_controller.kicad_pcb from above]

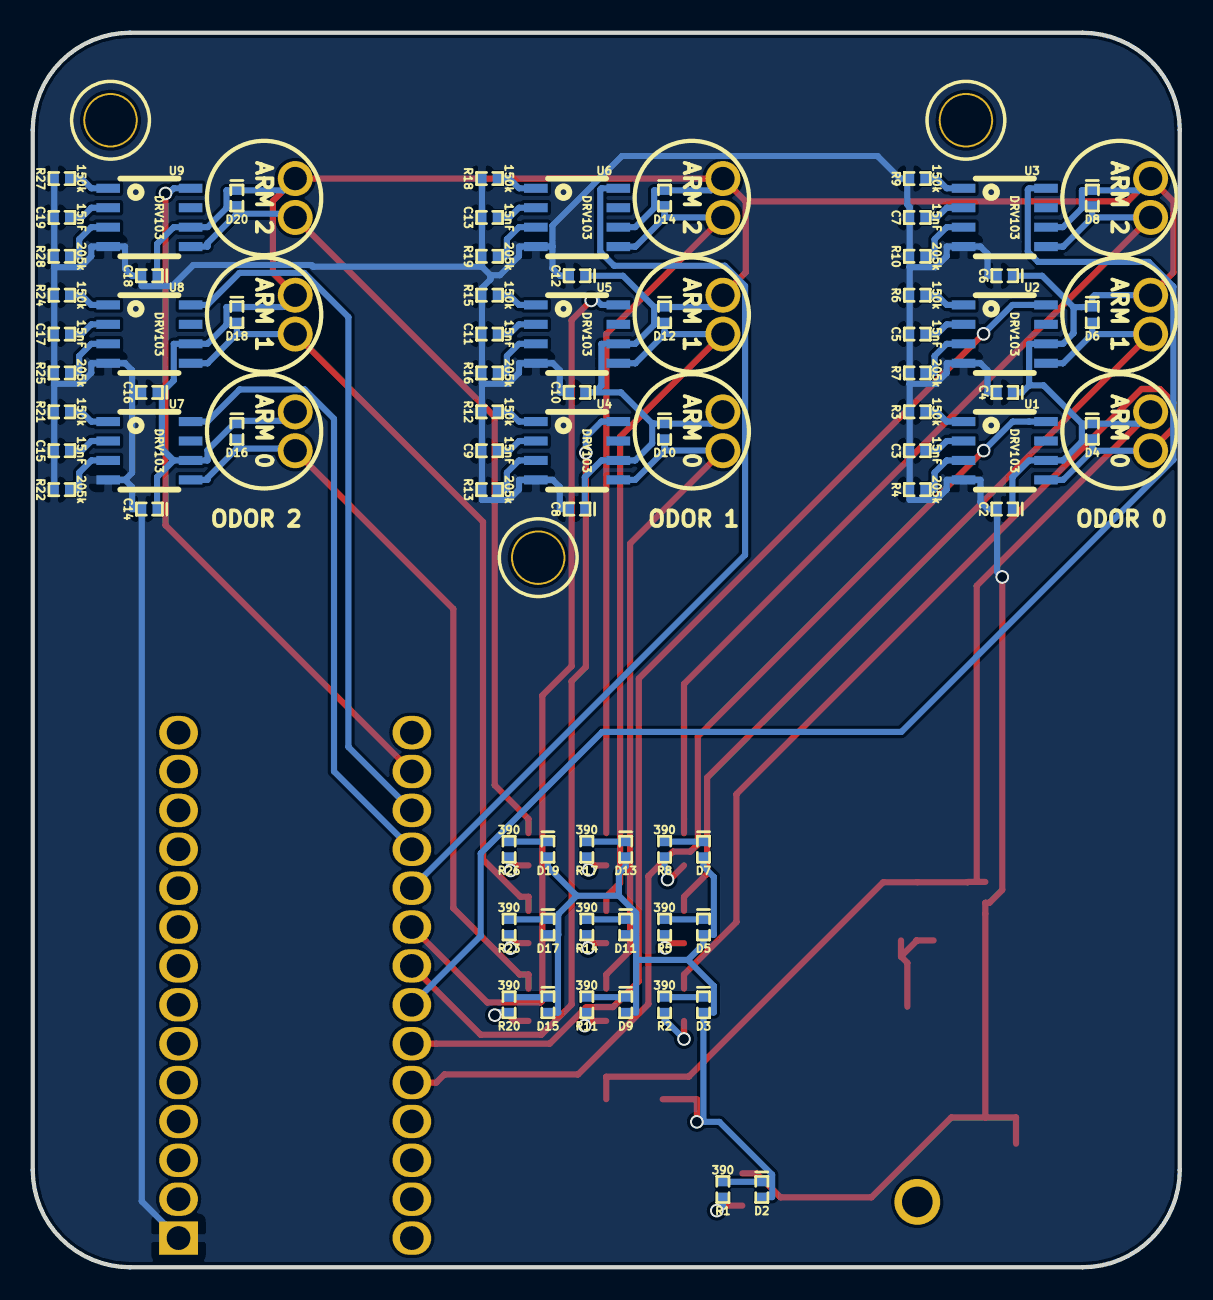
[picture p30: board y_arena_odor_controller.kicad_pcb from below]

Board: 2 copper layers, 74.9 x 80.6 mm, 105 parts (77 on the bottom side), 69 nets.

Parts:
C1: 10uF; SM0805
C2, C4, C6, C8, C10, C12, C14, C16, C18: 1uF; SM0402_POL
C3, C5, C7, C9, C11, C13, C15, C17, C19: 15nF; SM0402
D1: DIODE_SCHOTTKY_45V_10A; CFP15
D2, D3, D5, D7, D9, D11, D13, D15, D17, D19: DIODE_LOW_REV_CURRENT_0402; SM0402_POL
D4, D6, D8, D10, D12, D14, D16, D18, D20: DIODE_SCHOTTKY_0402; SM0402_POL
FID1, FID2, FID3, FID4: FIDUCIAL
L1, L2, L3, L4, L5, L6, L7, L8, L9, L10: LED_GRN; LED0805
MH1, MH2, MH3: VAL**; MOUNTING_HOLE_4-40
P1: PWR_JACK_2.1x5.5_SMD_RA; DCJACK_3PAD_SMD_RA
R1, R2, R5, R8, R11, R14, R17, R20, R23, R26: 390; SM0402
R3, R6, R9, R12, R15, R18, R21, R24, R27: 150k; SM0402
R4, R7, R10, R13, R16, R19, R22, R25, R28: 205k; SM0402
S1, S2, S3, S4, S5, S6, S7, S8, S9: VAL**; LEECO_LHDB
SW1: SPDT_SLIDE_500A_SM
TEENSY1: TEENSY_4.0
U1, U2, U3, U4, U5, U6, U7, U8, U9: DRV103; SOIC_8

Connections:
/ARM_0_ODOR_0: TEENSY1.22, U1.8
/ARM_0_ODOR_1: TEENSY1.21, U2.8
/ARM_0_ODOR_2: TEENSY1.20, U3.8
/ARM_1_ODOR_0: TEENSY1.19, U4.8
/ARM_1_ODOR_1: TEENSY1.18, U5.8
/ARM_1_ODOR_2: TEENSY1.17, U6.8
/ARM_2_ODOR_0: TEENSY1.16, U7.8
/ARM_2_ODOR_1: TEENSY1.15, U8.8
/ARM_2_ODOR_2: TEENSY1.14, U9.8
/Vled: D2.2, D3.2, D5.2, D7.2, D9.2, D11.2, D13.2, D15.2, D17.2, D19.2, SW1.1
/odor_0/SH: D4.2, L2.2, S1.1, U1.5
/odor_1/SH: D6.2, L3.2, S2.1, U2.5
/odor_2/SH: D8.2, L4.2, S3.1, U3.5
/odor_3/SH: D10.2, L5.2, S4.1, U4.5
/odor_4/SH: D12.2, L6.2, S5.1, U5.5
/odor_5/SH: D14.2, L7.2, S6.1, U6.5
/odor_6/SH: D16.2, L8.2, S7.1, U7.5
/odor_7/SH: D18.2, L9.2, S8.1, U8.5
/odor_8/SH: D20.2, L10.2, S9.1, U9.5
GND: C1.2, C2.2, C3.2, C4.2, C5.2, C6.2, C7.2, C8.2, C9.2, C10.2, C11.2, C12.2, C13.2, C14.2, C15.2, C16.2, C17.2, C18.2, C19.2, L1.2, P1.2, R3.2, R4.2, R6.2, R7.2, R9.2, R10.2, R12.2, R13.2, R15.2, R16.2, R18.2, R19.2, R21.2, R22.2, R24.2, R25.2, R27.2, R28.2, TEENSY1.GND, U1.4, U2.4, U3.4, U4.4, U5.4, U6.4, U7.4, U8.4, U9.4
unnamed: C3.1, U1.2
unnamed: C5.1, U2.2
unnamed: C7.1, U3.2
unnamed: C9.1, U4.2
unnamed: C11.1, U5.2
unnamed: C13.1, U6.2
unnamed: C15.1, U7.2
unnamed: C17.1, U8.2
unnamed: C19.1, U9.2
unnamed: D2.1, R1.1
unnamed: D3.1, R2.1
unnamed: D5.1, R5.1
unnamed: D7.1, R8.1
unnamed: D9.1, R11.1
unnamed: D11.1, R14.1
unnamed: D13.1, R17.1
unnamed: D15.1, R20.1
unnamed: D17.1, R23.1
unnamed: D19.1, R26.1
unnamed: L1.1, R1.2
unnamed: L2.1, R2.2
unnamed: L3.1, R5.2
unnamed: L4.1, R8.2
unnamed: L5.1, R11.2
unnamed: L6.1, R14.2
unnamed: L7.1, R17.2
unnamed: L8.1, R20.2
unnamed: L9.1, R23.2
unnamed: L10.1, R26.2
unnamed: R3.1, U1.1
unnamed: R4.1, U1.3
unnamed: R6.1, U2.1
unnamed: R7.1, U2.3
unnamed: R9.1, U3.1
unnamed: R10.1, U3.3
unnamed: R12.1, U4.1
unnamed: R13.1, U4.3
unnamed: R15.1, U5.1
unnamed: R16.1, U5.3
unnamed: R18.1, U6.1
unnamed: R19.1, U6.3
unnamed: R21.1, U7.1
unnamed: R22.1, U7.3
unnamed: R24.1, U8.1
unnamed: R25.1, U8.3
unnamed: R27.1, U9.1
unnamed: R28.1, U9.3
VAA: D1.2, P1.1
VCC: C1.1, C2.1, C4.1, C6.1, C8.1, C10.1, C12.1, C14.1, C16.1, C18.1, D1.1, D4.1, D6.1, D8.1, D10.1, D12.1, D14.1, D16.1, D18.1, D20.1, S1.2, S2.2, S3.2, S4.2, S5.2, S6.2, S7.2, S8.2, S9.2, SW1.2, U1.6, U2.6, U3.6, U4.6, U5.6, U6.6, U7.6, U8.6, U9.6

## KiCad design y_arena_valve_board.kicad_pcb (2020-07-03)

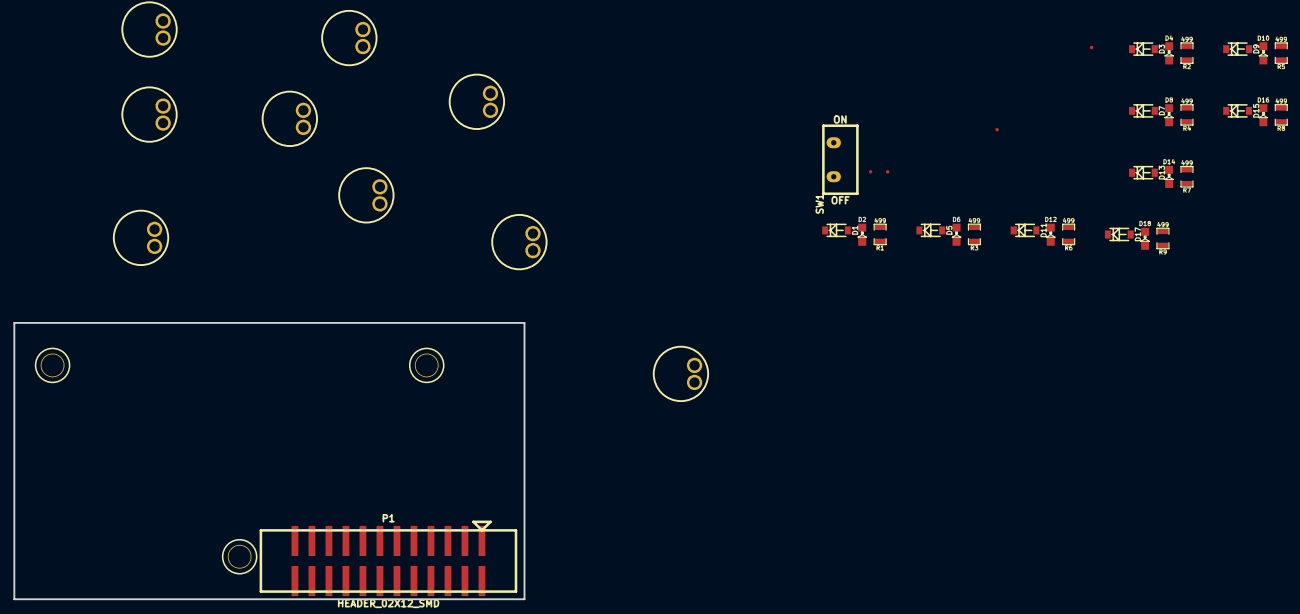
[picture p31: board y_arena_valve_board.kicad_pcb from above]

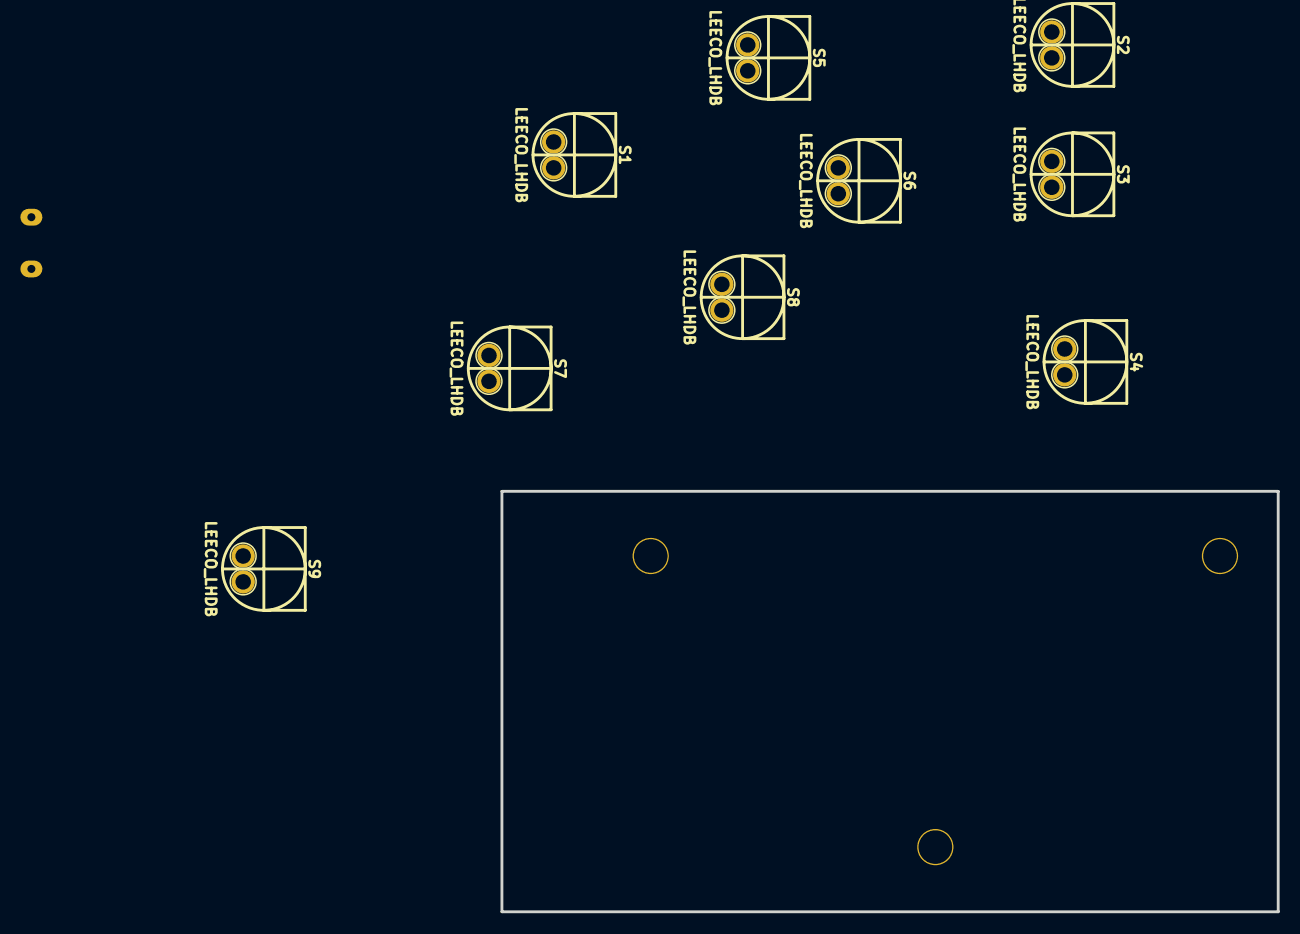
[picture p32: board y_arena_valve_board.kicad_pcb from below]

Board: 2 copper layers, 76.2 x 41.3 mm, 45 parts (9 on the bottom side), 29 nets, no tracks yet.

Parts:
D1, D3, D5, D7, D9, D11, D13, D15, D17: diode_low_rev_current; SOD-123
D2, D4, D6, D8, D10, D12, D14, D16, D18: LED_GRN; LED0805
FID1, FID2, FID3, FID4: FIDUCIAL
MH1, MH2, MH3: MOUNTING_HOLE_4-40
P1: HEADER_02X12_SMD; HEADER_02x12_SMD
R1, R2, R3, R4, R5, R6, R7, R8, R9: 499; SM0805
S1, S2, S3, S4, S5, S6, S7, S8, S9: LEECO_LHDB
SW1: SPST_SLIDE_AS

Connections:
/VALVE_0: D2.2, P1.2, S1.2
/VALVE_1: D4.2, P1.4, S2.2
/VALVE_2: D6.2, P1.6, S3.2
/VALVE_3: D8.2, P1.8, S4.2
/VALVE_4: D10.2, P1.10, S5.2
/VALVE_5: D12.2, P1.12, S6.2
/VALVE_6: D14.2, P1.14, S7.2
/VALVE_7: D16.2, P1.16, S8.2
/VALVE_8: D18.2, P1.18, S9.2
LED_PWR: D1.2, D3.2, D5.2, D7.2, D9.2, D11.2, D13.2, D15.2, D17.2, SW1.3
unnamed: D1.1, R1.1
unnamed: D2.1, R1.2
unnamed: D3.1, R2.1
unnamed: D4.1, R2.2
unnamed: D5.1, R3.1
unnamed: D6.1, R3.2
unnamed: D7.1, R4.1
unnamed: D8.1, R4.2
unnamed: D9.1, R5.1
unnamed: D10.1, R5.2
unnamed: D11.1, R6.1
unnamed: D12.1, R6.2
unnamed: D13.1, R7.1
unnamed: D14.1, R7.2
unnamed: D15.1, R8.1
unnamed: D16.1, R8.2
unnamed: D17.1, R9.1
unnamed: D18.1, R9.2
VAA: P1.1, P1.3, P1.5, P1.7, P1.9, P1.11, P1.13, P1.15, P1.17, P1.19, P1.21, P1.23, S1.1, S2.1, S3.1, S4.1, S5.1, S6.1, S7.1, S8.1, S9.1, SW1.1

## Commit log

2020-06-25 Add mechanical files
    [valve_assembly.stp, valve_pcb.dxf]
2020-06-25 Update mechanical files
    [compound_y_valve_board.kicad_pcb, compound_y_valve_board.sch, valve_pcb.dxf]
2020-06-29 Move files
    [compound_y_valve_board.kicad_pcb, compound_y_valve_board.sch]
2020-06-29 Moved files
    [compound_y_valve_board.kicad_pcb, compound_y_valve_board.sch]
2020-06-29 Progress towards v1.0
    [compound_y_valve_board.sch]
2020-06-30 compound_y_valve_board -> y_arena_controller_pi
    [y_arena_controller_pi.kicad_pcb, y_arena_controller_pi.sch]
2020-06-30 Copy components and footprints from power_switch_controller
    [raspberry_pi_with_power.sch, y_arena_controller_pi.sch]
2020-07-01 Update raspberry_pi_with_power
    [raspberry_pi_with_power.sch]
2020-07-01 y_arena_controller_pi -> y_arena_valve_board
    [raspberry_pi_with_power.sch, y_arena_valve_board.kicad_pcb, y_arena_valve_board.sch]
2020-07-01 Add header
    [valve_with_led.sch, y_arena_valve_board.sch]
2020-07-02 Initial pcb import
    [supplemental_digikey_parts.csv, valve_with_led.sch, y_arena_valve_board.kicad_pcb, y_arena_valve_board.sch]
2020-07-03 Add footprints to test
    [y_arena_valve_board.kicad_pcb]
2020-07-13 y_arena_valve_board -> y_arena_valve_controller
    [valve_with_led.sch, y_arena_valve_controller.kicad_pcb, y_arena_valve_controller.sch]
2020-07-13 Add Teensy 4.0
    [valve_with_led.sch, y_arena_valve_controller.sch]
2020-07-13 Add schematics
    [power_switches.sch, valve_with_led.sch, y_arena_valve_controller.sch]
2020-07-13 First draft of schematic
    [power_switches.sch, valve_with_led.sch, y_arena_valve_controller.kicad_pcb, y_arena_valve_controller.sch]
2020-07-17 Remove teensy and add power input
    [power_switches.sch, valve_with_led.sch, y_arena_valve_controller.sch]
2020-07-17 Add phidget
    [valve_with_led.sch, y_arena_valve_controller.kicad_pcb, y_arena_valve_controller.sch]
2020-07-20 Updated libraries
    [y_arena_valve_controller.kicad_pcb]
2020-07-20 Finished schematic v1.0
    [4_Y_ARENA_STAND.stp, valve.sch, valve_with_led.sch, y_arena_valve_controller.dsn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]
2020-07-21 Finished ver 1.0
    [Digi-Key_parts.csv, bom.csv, supplemental_Digi-Key_parts.csv, valve.sch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]
2020-07-21 Progress towards v1.1
    [Digi-Key_parts.csv, bom.csv, valve.sch, y_arena_valve_controller-B_Cu.gbl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]
2020-07-21 Finished v1.1
    [valve.sch, y_arena_valve_controller.kicad_pcb, y_arena_valve_controller.sch]
2020-07-21 Finishing up BOM
    [supplemental_Digi-Key_parts.csv, supplemental_Phidgets_parts.csv]
2020-07-22 Add parts to BOM
    [Digi-Key_order.csv, Digi-Key_parts.csv, Phidgets_order.csv, bom.csv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]
2020-07-31 Finished schematic v1.2
    [valve_spike_hold.sch, y_arena_valve_controller.sch]
2020-07-31 Updated parts
    [Digi-Key_order.csv, Digi-Key_parts.csv, Phidgets_order.csv, bom.csv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]
2020-08-01 Use 0402 parts instead of 0805
    [valve_spike_hold.sch, y_arena_valve_controller.kicad_pcb, y_arena_valve_controller.sch]
2020-08-01 Ready to route
    [supplemental_Digi-Key_parts.csv, valve_spike_hold.sch, y_arena_valve_controller.kicad_pcb, y_arena_valve_controller.sch]
2020-08-01 Route tracks and zones
    [y_arena_valve_controller.dsn, y_arena_valve_controller.kicad_pcb]
2020-08-02 Use surface mount slide switch and barrel jack
    [valve_spike_hold.sch, y_arena_valve_controller.kicad_pcb, y_arena_valve_controller.sch]
2020-08-02 Finished routing
    [valve_spike_hold.sch, y_arena_valve_controller.dsn, y_arena_valve_controller.kicad_pcb, y_arena_valve_controller.sch]
2020-08-02 Documentation ready but flaw in bom
    [Digi-Key_parts.csv, bom.csv, supplemental_Digi-Key_parts.csv, y_arena_valve_controller-B_Cu.gbl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]
2020-08-03 Finished version 1.2
    [Digi-Key_parts.csv, bom.csv, y_arena_valve_controller-B_Cu.gbl, y_arena_valve_controller-B_Mask.gbs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]
2020-08-06 Updated supplemental bom
    [Digi-Key_order.csv, supplemental_Digi-Key_parts.csv]
2020-08-14 Add position file in csv format
    [y_arena_valve_controller-all-pos.csv]
2020-08-18 Use new usb hub part
    [supplemental_Digi-Key_parts.csv]
2020-08-19 Rename VALVE lines from VALVE_0 -> ARM_0_VALVE_0
    [y_arena_valve_controller.dsn, y_arena_valve_controller.kicad_pcb, y_arena_valve_controller.sch]
2020-09-02 Added board images to documentation
    [supplemental_Digi-Key_parts.csv]
2020-11-19 Complete v1.3
    [Digi-Key_order.csv, odor_spike_hold.sch, supplemental_Digi-Key_parts.csv, y_arena_odor_controller-B_Cu.gbl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]
